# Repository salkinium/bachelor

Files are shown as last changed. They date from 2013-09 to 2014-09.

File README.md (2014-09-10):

Bachelor Thesis Source Code
===========================

This repository contains the entire source code of my bachelor thesis "Temperature Dependency of Bit Error Distributions in Wireless Sensor Networks".

Organisation
------------

This repository is organized as follows:

-	The *box* folder contains the PCB schematics and the CAD drawings and embedded software for the heat box,
- The *experiment_control* folder contains the python software for the experiment server and data logger,
- The *link_analysis* folder contains the python software for analyzing and visualizing experiment results,
- The *motes* folder contains the TinyOS source code for the WSN motes,
- The *position* folder contains CAD drawings of the WSN mote holder,
- The *thesis* folder contains the entire latex source code for my thesis.

[Thesis as PDF](https://github.com/salkinium/bachelor/raw/master/thesis/thesis.pdf).

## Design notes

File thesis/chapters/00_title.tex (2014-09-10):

\titlehead{
	\centering
	
	\hfill
	
} % end titlehead

\begin{titlepage}

\let\footnotesize\small \let\footnoterule\relax

\hbox{}
\vfill

\centering

\begin{doublespace} 
{ \huge\textbf{\textsf{Temperature Dependency \\ \vspace{-0.4em}
of Bit Error Distributions \\ \vspace{-0.4em}
in Wireless Sensor Networks \\ \vspace{-0.4em}}}}
\end{doublespace}
\vskip 2cm

{\large Bachelor Thesis\\[5pt]}
{\large \textbf{Niklas Hauser}}
\vskip 1cm

\textbf{RWTH Aachen University, Germany\\[5pt]
        Chair of Communication and Distributed Systems}
\vskip 2cm

\large

Advisors:
\vskip 2mm

\begin{tabular}{R{7cm}p{7cm}}
Dr. & Matteo Ceriotti\\
Dipl.-Inform. & Florian Schmidt\\
Prof.~Dr.-Ing. & Klaus Wehrle\\
Prof.~Dr.~rer.~nat. & Bernhard Rumpe
\end{tabular}
\vskip 1cm

\begin{tabular}{R{6cm}p{6cm}}
Registration date:  & January 29, 2014 \\
Submission date:    & May 29, 2014 \\
\end{tabular}

\vfill

\end{titlepage}

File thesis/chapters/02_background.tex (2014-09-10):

\chapter{Background}
\label{chap:background}

This work centers around investigating and improving the quality of corrupted communications in low power networks.
Therefore this chapter will provide the necessary background information on the form of communication used in \acl{WSN}s and the radio and microcontroller hardware we employed in our study.
Furthermore, we shortly describe what approaches to \acl{ECC}s exist and how they work.

\section{\acl{WSN}s}

A \acf{WSN} comprises of two or more nodes, called \emph{motes}, which can communicate using low power radio communication.
This provides a means to easily deploy sensing, actuating and communication infrastructures in a given space.
The nodes are mostly powered by small and simple microcontrollers connected to a radio and other peripherals such as sensors and actuators as shown in Figure~\ref{fig:mote_schematic}.

Networked motes communicate with their neighboring motes and can address the whole network via multi-hop transmissions, therefore deprecating the use of expensive wired buses.
However, due to the nature of wireless communication, the software must be built to tolerate unreliable communication links, which can change network topology and result in high latency in data exchanges or a complete loss of communication.

Integrated batteries are used to power the motes for a certain amount of time when deployed in areas where access to a power grid is too costly or impossible.
Especially for these battery powered applications, conserving energy is a high priority and places tight restrictions on the type of CPU and radio transmission power and duty cycle, effectively limiting communication range and bandwidth.

A typical application for a \ac{WSN} would be the collection of meteorological information over large inaccessible areas, such as forests, or the monitoring of large industrial complexes to reduce the cost of wiring~\cite{Boano2009}.
The high effort required to exchange empty batteries in these scenarios demands energy-aware programming, which keeps the overall energy consumption to a minimum.

\begin{figure}[t]
	\tikzset{
		boxt/.style={
	           rectangle,
	           fill=white,
	           draw=black, thick,
	           text width=2cm,
	           minimum height=1cm,
	           text centered},
	}
	\centering
	\begin{tikzpicture}[>=stealth',
	<->,
	shorten <=1pt,
	shorten >=1pt]
		% \draw (0,0) rectangle (7,5);
		\node[boxt, fill=slightgray] (controller) at (4, 4.3) {$\mu$Controller};
		\node[boxt] (sensors) at (5.7, 2.8) {Sensors};
		\node[boxt] (actuators) at (5.7, 1.7) {Actuators};
		\node[boxt, fill=slightgray] (radio) at (2.3, 1.7) {Radio};
		\node[boxt] (storage) at (2.3, 2.8) {Storage};
		\node (antenna) at (0.4, 3.5) {};
		\node[font=\small] (uart) at (6.35, 4.65) {UART};

		\draw (1,1) rectangle (7,5);
		\draw[thick] (1,0) rectangle (7,0.9) node[midway] {Power Source};

		\draw[thick] (controller.east) -| (sensors.north);
		\draw[thick] (controller.west) -| (storage.north);
		\draw[thick] ($(controller.south west)!0.45!(controller.south east)$) |- (radio.east);
		\draw[thick] ($(controller.south west)!0.55!(controller.south east)$) |- (actuators.west);
		\draw[thick, ->] ($(controller.south east)!0.8375!(controller.north east)$) -- (uart.west);

		\draw[very thick, -, shorten <=0pt, shorten >=-3pt] (radio) -| (antenna);
		\fill[color=black] (antenna) circle (0.075);
		\draw[dashed] (antenna) circle (0.15);
		\draw[dashed] (antenna) circle (0.25);
		\draw[dashed] (antenna) circle (0.35);
		\draw[dashed] (antenna) circle (0.45);

	\end{tikzpicture}
	\caption{A schematic representation of a mobile \acs{WSN} mote with a power source.}
	\label{fig:mote_schematic}
\end{figure}

\section{Communications}

Since this works focuses heavily on communications between motes, we use specific terms to help describe its properties.

A \emph{packet} is the basic unit of communication between two motes, containing metadata, such as sender and addressee, and payload.
A \emph{message} is the interpretation of the payload of one or several packets.
If a message is very long, it might be fragmented into several packets, however, in all our experiments, one message uses only one packet.
We define a \emph{link} as the transmission of messages from one mote addressed to another over a period of time, even when none of these messages where received by the addressee, due to channel effects or connection problems.

\subsection{IEEE 802.15.4 Standard}

In this work we use the CC2420 wireless transceiver~\cite{cc2420}, a very common communication radio in \acp{WSN}.
The CC2420 implements the \ac{IEEE} 802.15.4 standard and uses \ac{OQPSK} modulation in the \SI{2.4}{\giga\hertz} ISM band with a nominal data rate of \SI{250}{\kilo bit\per\second}.

The \ac{PPDU} is the lowest accessible layer as shown in Figure~\ref{fig:packet_format} with a maximum size of 133 bytes.
This leaves 127 bytes for the \ac{MPDU} and between 102 and 122 bytes for the frame payload.
To increase robustness of transmission, each byte is split into two 4-bit symbols, which are then mapped to a 32-bit chip sequence and modulated using \ac{OQPSK}.

These 32-bit chip sequences are part of \ac{IEEE} 802.15.4 and were chosen to produce high Hamming distances against each other, so that bit errors can already be corrected within the received chip sequence to some degree. 
The higher the Hamming distance between two sequences, the less likely they are to be mistaken for one another.
Therefore a corrupted 4-bit symbol is only received, when a corrupted chip sequence is mistaken for another sequence, which requires several bits of the 32-bit sequence to be flipped.
The minimum Hamming distance between two sequences is 12 bit, the maximum is 20 bit~\cite{Schmidt2013}.

At the beginning of every transmission, a Preamble Sequence is modulated, which triggers a listening mote to synchronize and receive this new packet.
Typical reasons for not receiving packets are either the reception of a signal with too little power to be noticeable above the channel noise, or the reception of a corrupted preamble, so that the listening mote does not start receiving a packet, even though the power levels would permit it.

When a packet is received, its \ac{FCS} is automatically evaluated to check for bit errors introduced by channel noise.
However, a failed \ac{FCS} test can also be the results of a corrupted Frame Length field.
This prompts the radio to read in too few or too many bytes, thereby comparing the \ac{FCS} results to the wrong bytes at, what the receiver wrongly considers the ``end'' of the packet.

Even though the \ac{FCS} is evaluated for all messages automatically, the CC2420 allows retrieval of corrupted messages, including all hardware link qualifiers such as \ac{LQI} and \ac{RSSI}.
We make use of this ability to analyze the content of these corrupted messages in our work.

\begin{figure}[t]
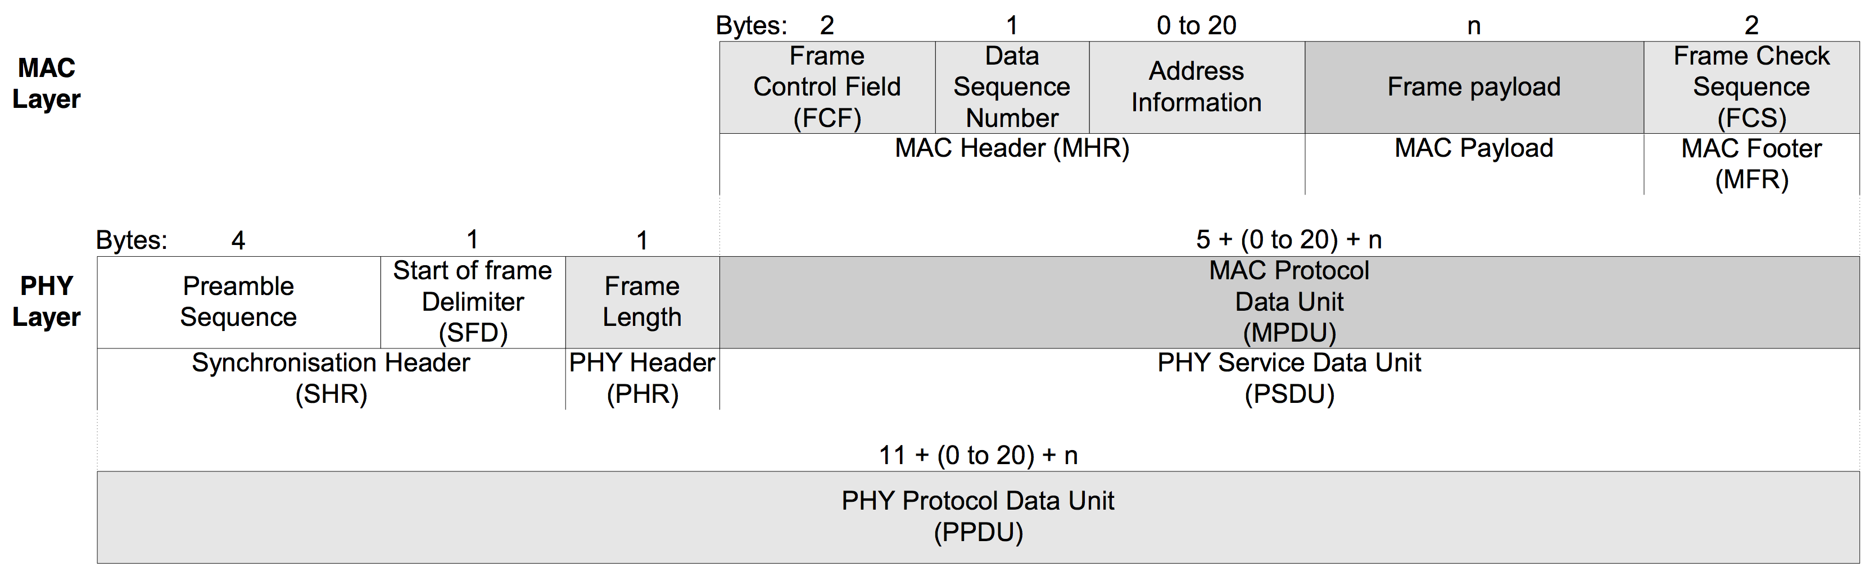
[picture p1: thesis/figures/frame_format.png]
	
	\caption{The packet format implemented defined by \acs{IEEE} 802.15.4 taken from \cite{cc2420}.}
	\label{fig:packet_format}
\end{figure}

\subsection{\acs{UART} Communication}

The microcontroller can also communicate over a wired bus using its \ac{UART} module.
\ac{UART} does not provide a seperate clock line (hence \emph{asynchronous}), which requires the receiver to synchronize itself at the beginning of each symbol transfer and sample the signal at multiples of the baudtime $t_{symbol} = f_{Clock} / f_{BaudRate}$, which derives from the \emph{baudrate} of the transmitter.
Here the receiver synchronizes on the falling edge of the start bit, which is always low, and has to sample the successive bits at the just right time, as shown in Figure~\ref{fig:uart_timing}.
If the transmitter's and/or receiver's clock is running too slow or too fast, then $t_{Symbol}$ is too small or too large, resulting in a corrupted sampling of the bits in the symbol as marked in red.

The relative error tolerance for the 8N1 configuration shown in the Figure (8 databits, 1 startbit and 1 stopbit) is $\pm5\%$, since the sample point of the stop bit may only shift by at most $\pm t_{Symbol}/2$.
With 10 bits to read, one $t_{Symbol}$ equals one tenth of the symbol transmission time, hence a relative tolerance of $\pm5\%$.
For example, the tolerance for 7-bit transfers (9 baudtimes) increases to $\pm5.56\%$.

However, since both transmitter and receiver may experience clock drift, the error must not exceed $5\%$ in total, which in the worst case of opposing clock drift directions (one too fast, one too slow) imposes a tight allowed deviation of $+2.5\%$ and $-2.5\%$ on the modules respectively.
In practice, \ac{UART} can therefore be difficult to use with uncorrected or unknown clock drifts.

\begin{figure}[t]
	% \centering
	\begin{tikzpicture}[thick, >=stealth']
		\draw[white] (-4.5,-0.75) -- (-3,-0.75);

		\def \di {0.46}
		\def \dii {0.535}

		\fill[slightgray] (1,2) rectangle (1.5,3) node[midway, black] {S};
		\fill[slightgray] (5.5,2) rectangle (6,3) node[midway, black] {P};

		\foreach \s in {0,...,7}
		{
			\draw (1.5+\s*0.5,2) rectangle (2+\s*0.5,3) node[midway] {\s};
		}

		\draw[-] (-1,3) -- (1,3) -- (1,2) -- (1.5,2);
		\draw[-] (5.5,3) -- (8,3);

		\path (-1,2) -- (1,3) node[midway, font=\tiny] {\textbf{IDLE}};
		\path (6,2) -- (8,3) node[midway, font=\tiny] {\textbf{IDLE}};

		\draw[->] (2.5,3.75) -- (7,3.75) node[midway, above, font=\small] {Time};

		\draw[->, shorten <=1pt, shorten >=1pt] (1,3.5) node[above, font=\small] {Sync} -- (1,3);

		\foreach \s in {0,...,9}
		{
			\filldraw (1.25+\s*0.5, 1.2) circle (0.06);
		}

		\draw[|<->|, shorten >=-0.4pt, shorten <=-0.4pt] (1,1.6) node[left=0pt, font=\small] {$t_{Symbol}$} -- (1.5,1.6);
		\draw[->, shorten >=3pt] (6.1, 1.65) node[right=0pt, font=\small] {Ideal Timing} -| (5.75, 1.2);

		\node[font=\small, right] at (-1,0.5) {Too Fast};
		\node[font=\small, right] at (-1,-0.2) {Too Slow};

		\fill[slightred, rounded corners] (1.25+\di*4.5+\di-0.5, 0.3) rectangle (1.25+\di*9.5+\di-0.5, 0.7);
		\foreach \s in {0,...,9}
		{
			\draw (1.25+\s*\di+\di-0.5, 0.5) circle (0.06);
		}

		\fill[slightred, rounded corners] (1.25+\dii*5.5+\dii-0.5, -0.4) rectangle (1.25+\dii*9.5+\dii-0.5, 0);
		\foreach \s in {0,...,9}
		{
			\draw (1.25+\s*\dii+\dii-0.5, -0.2) circle (0.06);
		}

		\foreach \s in {0,...,10}
		{
			\draw[line width=0.2pt] (1+\s*0.5,1.9) -- (1+\s*0.5,-0.6);
		}
	\end{tikzpicture}
	\caption{\acs{UART} timing diagram of the sampling points of an 8-bit symbol.}
	\label{fig:uart_timing}
\end{figure}

\section{Error Control Schemes}

There exist two approaches to improve the quality of an imperfect communication channel: using \ac{FEC} to add redundancy before transmission, so that bit errors can be \emph{detected} and \emph{corrected} by the receiver, and using \ac{ARQ} to only \emph{detect} bit errors, but request a retransmission, instead of correcting them.
While \ac{ARQ} is simple and requires very little computational and transmission overhead, it does perform poorly in conditions with a high channel error rate.
\ac{FEC} allows constant throughput at the expense of coding and decoding time and transmission overhead, depending on the specific \ac{ECC} used.
To overcome their individual disadvantages, these two approaches can be merged into \emph{hybrid} \ac{ARQ} schemes, however, in our work we will be focusing on using \ac{FEC} schemes alone.

The simplest \acp{ECC} belong to the class of linear cyclic coding schemes, where a bit stream is divided into non-overlapping blocks, which are then encoded separately.
The most widely used linear cyclic block codes are binary \ac{BCH} and non-binary \ac{RS} codes, both of which can be used to correct bit and burst errors.
There are several other approaches to \acp{ECC}, however, they go above the focus of this work.

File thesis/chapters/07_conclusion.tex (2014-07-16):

\chapter{Conclusion}

This work investigated the effects of temperature on bit error patterns and \ac{PRR} in the context of low power communications as used in \acp{WSN}.

We began with a description of the low-cost design of our testbed, which allows fine control of mote temperature, mote orientation and experiment execution.
This testbed was the foundation, which allowed us to create and control links with high \ac{BER} between CC2420 radios at different temperatures.
Due to problems with the serial communication between mote and PC, we measured microcontroller clock drift and found the \ac{DCO} calibration algorithm in TinyOS not to be working above \SI{55}{\celsius}, and provided and tested a correction method.

Then we showed that bit errors follow a distinct distribution, which is influenced by payload content, confirming findings by Schmidt~\etal~\cite{Schmidt2013} and extending them with a classification of pattern magnitudes.
We found two bit error patterns, which we did not know before, due to their rare occurrence.
Furthermore, we saw no influence of temperature on these patterns.

The experiments were completed with a detailed investigation into \ac{PRR} asymmetry, when transmitter and receiver were heated to different temperatures.
Our results showed that the receiver is more vulnerable to an increase in temperature than the transmitter, thereby disproving findings by Boano~\etal~\cite{Boano2013}.

We used these findings to create a trace-based simulator to study the effects of temperature on \ac{FEC} usage, and evaluated the simulators performance, which we found accurate.
Using traces of our real experiments, we simulated several \ac{RS} encoding strengths and compared them based on normalized throughput.
On this basis we proposed a minimum encoding strength of 12.5\% overhead, which is increased with temperature to a maximum of 25\% overhead.

% It seems we are missing a independent \ac{LQE} across platforms and testbeds.
% This exact problem has been summarized by Baccour~\etal{} in their survey~\cite{Baccour2012}.
% The authors come to the conclusions that of the hardware-based \ac{LQE}s, \ac{RSSI} has the worst accuracy, especially for intermediate links, and that \ac{LQI} is a better indicator of \ac{PRR} than \ac{RSSI}, as we have pointed out too.
% They come to the conclusion that software-based \ac{LQE}s are better at describing link quality than hardware-based \ac{LQE}s.

\newpage

\section*{Future Work}

The results of our experiment warrant further investigations into several topics.

In Section~\ref{sec:link_quality} we briefly described the difficulty we encountered in creating a link with the right \ac{BER} even when using our mote harness from Section~\ref{sec:mote_harness}.
An interesting addition to this harness could be a motor controlled z-axis to further automate link quality selection via antenna orientation in a closed-loop controller setup.
In that respect, it might be more practical to rebuild this harness partially out of LEGO Technic parts, which would make the mechanic aspects of this function much easier.

Concerning the limitations of the \ac{DCO} calibration algorithm of TinyOS described in Section~\ref{sec:clock_drift}, we filed a bug report on their open-source project page.
We hope that this raises awareness of the algorithm's performance and prompts a fix.

In Section~\ref{subsec:pattern_anomalies} we described two bit error patterns, which were very different to what we recorded in all other experiments we ran.
Further investigation is required to understand what creates these patterns and whether they exhibit different Hamming distances than described by Schmidt~\etal~\cite{Schmidt2013} and Hermans~\etal~\cite{Hermans2014}.

Further work is required to validate our proposals regarding temperature dependent \ac{RS} coding overhead using simulation and real experiments.
Even though our simulation was accurate enough for our conclusions, they were based on four real traces, which certainly do not cover all possible link qualities that can be expected in real world deployments.

% It is important to notice, that in regions with high link quality, especially at low temperature, \ac{ARQ} might outperform \ac{FEC} in energy efficiency as reported by Tian~\etal~\cite{Tian2008}.
% Therefore our results might be best deployed in a hybrid \ac{ARQ} scheme~\cite{Liu1997}, where \ac{FEC} is only deployed once the temperature reaches a certain threshold.

% \todo{we logged all raw data, so we could use it to test software-based \ac{LQE}s~\cite{Baccour2012}}

% \todo{Correlation threshold of the CC2420 can be user defined~\cite{Liang2010}}

% This link asymmetry can lead to some interesting situations, where a mote at high temperature is able to transmit messages, but not receive them.
% Looking at their own temperature, mote would receive another hint in whether the lack of received messages is caused by a missing transmitter, or by its own disability to receive messages.
% For example, when no messages are received after a timeout, a failure of the transmitter is more likely when the receiver is at low temperature than at high temperatures.

% In a system that makes smart decisions based on information from multiple motes, such information could be used to judge whether the system is still functionally intact and then trigger a backup program, which reacts autonomously to the local sensor data collected but still notifies the rest of the network of its actions.
% Motes that are not in this backup mode can very likely receive these transmissions and augment the group decisions with the constraints of these autonomously acting motes.
% Therefore a failure of the entire system is delayed or prevented, by using controlled degradation of the system, which might not be as smart as before, but at least still providing a rudimentary service.

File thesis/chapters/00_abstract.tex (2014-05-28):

\cleardoublepage

% \selectlanguage{german}

\begin{center}
\paragraph{Kurzfassung}
\hrulefill

\end{center}

Mit der Verfügbarkeit von leistungsfähigen eingebetteten Geräten und kostengün\-stigen Funkmodulen, beginnen auch immer mehr batteriebetriebene Sensorgeräte miteinander zu reden und Probleme gemeinsam zu entscheiden.
Es ist abzusehen, dass die Benutzung solcher intelligenten Geräte in drahtlosen Sensornetzwerken in\-dustrielle Prozesse vereinfachen und unsere Lebensqualität verbessern wird.

Allerdings ist die Laufzeit dieser mobilen Geräte durch ihre endliche Energiequelle, die meist nur mit viel Aufwand zu wechseln ist, beschränkt. Daher braucht es eine Programmierung, die energiebewusst kommuniziert, um die Lebensdauer der Bat\-terie so weit wie möglich zu verlängern.
Drahtlose Kommunikation ist stark durch Umweltveränderungen, allen voran die Lufttemperatur, beinflussbar, was zu Korrup\-tion oder Verlust von Paketen führen kann und ein erneutes Versenden des Pakets nach sich zieht.

In dieser Arbeit beschreiben wir eine kostengünstige Testplatform zum Testen der Funkverbindungen in einer temperaturkontrollierten Umgebung. Mit dieser Plat\-form untersuchen wir die Empfangsraten und die Bitfehlerverteilungen in korrupten Paketen.
Unsere Ergebnisse widerlegen frühere veröffentlichte Ergebnisse.
Schließ\-lich wenden wir diese Erkenntnisse auf die Programmierung eines Simulators an, mit dem wir untersuchen, wie sich Temperatur als Eingabegröße einer adaptiven Vorwärtsfehlerkorrektur verhält, um damit die Empfangsraten korrupter Pakete zu verringern.

% \selectlanguage{english}

\vspace {0.5cm}
\begin{center}
\paragraph{Abstract}
\hrulefill
\end{center}

With the availability of powerful embedded devices and inexpensive radio communication, ever more battery powered sensor devices make use of the added connectivity to talk to each other and decide problems collectively.
It is envisioned that usage of such smart devices in \acl{WSN}s will streamline industrial processes as well as improve our quality of life.

However, the runtime of these mobile devices is limited by their finite power source, which most often are impractical to exchange.
Therefore energy-aware programming and communication is required to prolong battery life for as long as possible.
Unfortunately, wireless communication is strongly influenced by environmental changes, most prominently air temperature, which can lead to packet corruption or loss and requires energy-consuming retransmissions.

In this work we describe a low-cost testbed for testing radio performance in a temperature-controlled environment, with which we examine packet reception rates and bit error distributions within packet corruption. Our results disprove previous published findings.
Finally, we apply these findings on building a simulator, with which we investigate using temperature as an input for an adaptive \acl{FEC} scheme to improve packet reception rates and thereby reduce unnecessary retransmissions.

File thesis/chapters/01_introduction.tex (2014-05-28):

\chapter{Introduction}

With the introduction of more powerful low-power embedded devices, such as small microcontrollers, and the increased availability of low-cost radio transceivers especially in the last decade, more and more applications have been developed that enrich their functionality by receiving input from our environments.
Such applications can help us to use natural resources, such as farm land or forests, more efficiently, or streamline industrial processes by retrofitting more data sampling points, or simply alarm us when we forget to water the plants at home.

Concepts of augmenting our environments with connected sensors and actuators have been talked about for many years, with the most prominent concept being the \ac{IoT}.
Here everyday objects are able to communicate with each other over local networks or the Internet and come to smart decisions collectively.
This infusion of information about the real into the virtual world will keep growing with many new and exciting ways to improve our quality of life.

However, these concepts are built on very new technology, which has to be understood to be improved for the next generation of such devices.
The common culprit of today's mobile devices are their battery lives.
Even though impressive advancements have been made, especially in the area of smart phones, charging or exchanging batteries is cumbersome at best, and, in regard to sensor devices, impractical when they are distributed over large areas.
It is therefore imperative to extend battery life for as long as possible, which means not only using low-power hardware, but also merging it with energy-efficient software.

Fortunately, long and intensive computations do not have to be performed on the sensor devices locally, but can be delegated to a server connected to the power grid.
For that however, the sensor nodes must communicate using radio communication, which is by the laws of physics and electrical engineering still inherently energy-inefficient, especially compared to wired communication.

What sounds simple actually is complicated by the fact that radio communication is at the mercy of the environment, which introduces noise into the signal and strongly influences signal propagation.
Further complications arise with different antenna designs, the limitations of the modulation scheme and non-linearities in analog circuitry.
This leads to packets being corrupted or not being received at all, requiring the retransmissions of the original packet until it is received error-free.
However, in conditions of poor link quality this might not even be possible.
Hence, to reduce energy consumption, radio communication, especially retransmissions, must be kept to a minimum while not impairing functionality of the original application.

Additionally, a typical \acl{WSN} is deployed outside and its nodes are protected by air-tight containers from precipitation.
On a sunny day, temperatures inside these containers can climb well above outside air temperature, which influence radio and microcontroller performance quite dramatically.
In this thesis we focus on what impact temperature has on patterns in packet corruption and describe the experiments we created to study these patterns.
We analyze the results and try to improve link quality using \acl{FEC}.

The main contributions of this thesis are:
\begin{enumerate}
  \item
  the creation of a low-cost testbed for testing radio performance in a temperature-controlled environment (Chapter~\ref{chap:testbed}),
  
  \item
  the investigation of microcontroller clock drift, and the limitations of its calibaration in TinyOS (Chapter~\ref{chap:experiments}),

  \item
  the detailed analysis of the effects of temperature on bit error patterns and \acl{PRR}, which disproves published findings by Boano \etal~\cite{Boano2013} (Chapter~\ref{chap:experiments}),
  
  \item
  the modeling of the discovered patterns using a simulator (Chapter~\ref{chap:forward_error_correction}), and

  \item
  the investigation of using an adaptive \acl{FEC} scheme to improve throughput in temperature-influenced link conditions (Chapter~\ref{chap:forward_error_correction}).
\end{enumerate}

We provide the necessary background knowledge required for understanding our work in in Chapter~\ref{chap:background}, before briefly discussing previous, related work in Chapter~\ref{chap:related_work}.

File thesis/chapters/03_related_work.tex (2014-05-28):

\chapter{Related Work}
\label{chap:related_work}

The research field of investigating influences of the environment on wireless link quality is large and spans many technologies and protocols.
However, we focus on technologies deployed in low power networks such as \ac{WSN}s, where the advances in small and affordable radio technology pushed research forward.
In a first step towards energy efficient, reliable communications, especially in battery powered applications, a deep understanding of why messages become corrupted is required.

Here we present research relating to the IEEE 802.15.4 protocol used in most \ac{WSN}s, especially in the three areas this work focuses on, namely, the influence of temperature on link quality and bit error distributions within corrupted messages, as well as the use of \ac{FEC} to counteract these effects.

\section{Effects of Temperature}

Bannister~\etal~\cite{Bannister2008} were one of the first to systematically investigate the effect of temperature on the performance of the CC2420 radio.
They connected two radios together via coaxial cable with attenuators and placed one of them in a thermal chamber with a temperature range of 25 to \SI{65}{\celsius} while measuring signal power using the \ac{RSSI}.
The results showed a reduction of output power by $4--$\SI{5}{\dBm} when the transmitter was heated, but only \SI{3}{\dBm} reduction in measured input power when the receiver was heated.
Boano~\etal~\cite{Boano2010} also investigated this behavior in 2010 in a real world deployment, but found no difference in \ac{RSSI} between transmitter and receiver.
However, both works point to a loss of gain in the CC2420 \ac{LNA} as the source of the reduction in signal powers at higher temperatures.

In a long-term outdoor study in 2013, Wennerstr{\"o}m~\etal~\cite{Wennerstrom2013} examined the correlation between \ac{RSSI} and \ac{PRR} and environmental factors, such as temperature, relative and absolute humidity, precipitation and sunlight.
They found that of all environmental factors, temperature had the strongest influence, with an increase in temperature causing a significant decrease in both \ac{RSSI} and \ac{PRR}.
This was further researched by Boano~\etal~\cite{Boano2013}, who focused on the impact of temperature on \ac{RSSI}, \ac{SNR}, Noise Floor, \ac{PRR} and \ac{LQI}.
They determined a negative impact of temperature on all these values and expanded their work by looking at the asymmetry of \ac{PRR} when heating the transmitter and receiver.
They found that the loss in \ac{PRR} was more pronounced when heating the transmitter than the receiver.

Finally, Z\'{u}\~{n}iga~\etal~\cite{Zuniga2013} created a summarizing report on the effect of environment variables on current \ac{WSN} motes.
Apart from including all previous findings, they also describe a substantial negative impact of temperature on microcontroller clock drift.
However, the CC2420 clock is compensated for temperature and experiences no such drift.

\section{Bit Error Distributions}

Liang~\etal~\cite{Liang2010} investigated bit error distributions in the context of 802.11 (WiFi) interference.
They found that packet collisions cause burst errors, due to 802.11 packets typically being much shorter than 802.15.4 packets, particularly in the beginning of a message.
This is due to the 802.11 sender deferring sending its packets until the 802.15.4 transmission completed, however only if the 802.15.4 sender is close enough so that its transmission power can be sensed by the 802.11 collision avoidance algorithm.
If the 802.11 sender cannot sense the 802.15.4 transmission, the authors show an even bit error distribution across the entire packet.

Schmidt~\etal~\cite{Schmidt2013} examined the bit error distributions within corrupted messages in their outdoor testbed of 20 TelosB devices.
Similar to Liang~\etal, they found that for random payload, \ac{BER} remains stable throughout message, however, within all 4-bit symbols, the \ac{MSB} is significantly less likely to break than the 3 \ac{LSB}.
In addition, symbols with \ac{MSB} set to 1 are more likely to break than symbols with \ac{MSB} set to 0.
This behavior creates very different Hamming distances between the broken symbols coded in 32-bit chip sequences than defined by the 802.15.4 standard.
The authors also looked at burst error distribution and found these errors not independently distributed, but skewed towards longer bursts.

Their findings then where further completed by Hermans~\etal~\cite{Hermans2014} with an understanding of why the Hamming distances are different than expected.
The authors discovered that the pattern fits, when their simulation of these patterns uses a \ac{MSK} instead of the \ac{OQPSK} demodulator suggested by the 802.15.4 standard.
The \ac{MSK} demodulator can correctly receive packets sent by an \ac{OQPSK} modulator, but it outputs different code words than defined by the standard.
The authors hypothesized that these code words then have to be translated using a table, which would create the distinct bit error patterns.

\section{\acl{FEC}}

The use of \ac{FEC} schemes in communication has been investigated before, however, the available limited resources on \ac{WSN} motes focus research in this area very much on coding and energy efficiency.

Jeong~\etal~\cite{Jeong2003} investigated the performance of single- and double-bit correcting \ac{ECC} on very early \ac{WSN} motes, not using the 802.15.4 standard.
They came to the conclusion, that using \ac{BCH} codes is simple to implement, but performs poorly when encountering burst errors.
Busse~\etal~\cite{Busse2006} then compared the performance of a Hamming code, an interleaved double-bit correction code and a \ac{RS} code using their \ac{WSN} and found the \ac{RS} code to be the most efficient of them, both in the length of the added overhead, as well as the error correction capabilities.

Using mathematical energy consumption modeling, Tian~\etal~\cite{Tian2008} showed that for small packet lengths ($<1023$ bytes) \ac{BCH} codes outperform \ac{ARQ}.
However, research by Ma~\etal~\cite{Ma2009} points to \ac{RS} being more energy efficient than \ac{BCH} codes, especially when considering the energy consumption of transmitting the coding overhead.

Ahn~\etal~\cite{Ahn2005} examined changing \ac{FEC} coding strength dynamically based on link quality properties.
Their adaptive \ac{FEC} algorithm outperformed several static \ac{RS} codes in simulation, as well as in real traces.
Liang~\etal~\cite{Liang2010} created and evaluated an efficient, TinyOS compatible \ac{RS} implementation, called TinyRS, during their research on bit error distributions mentioned before.

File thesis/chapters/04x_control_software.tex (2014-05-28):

\section{Control Software}
\label{sec:control_software}

The motes and temperature boxes are connected via USB-to-Serial converters to a computer, and controlled with a Python program using the TinyOS Python SDK~\cite{tinyos.net}.
Since all motes are connected to one computer, packet loss due to colliding transmissions is avoided via central scheduling of transmissions.
The software holds virtual representations of the mote, temperature controller and link, and logs experiment results to disk.
A simple scripting language allows the definition of commands that are interpreted by the runtime and executed serially so that experiments can be described in independent and compact form.
Multiple scripts can be added, so that experiments can run unsupervised around the clock.

During an experiment all transmissions and receptions are written to a log in ASCII format, which includes a timestamp, sending and receiving node ids, a sequence number, link quality metadata, mote temperature and the entire \ac{MPDU} payload, including \ac{FCS}.%, as shown in Listing~\ref{lst:log_example}.
These logs describe the entire experiment in a unprocessed format, which is then read by the evaluation scripts that reassemble them into messages and links.

This modular software setup allows for a lot of freedom when designing these experiments, as all evalutation data is based upon these unprocessed logs.
This enables us to use one experiment for multiple purposes by focusing on different parameters, of which we will make use later in in Chapter~\ref{chap:forward_error_correction}.

\begin{listing}[t]
\begin{lstlisting}[breaklines=true]
timestamp=2014-05-03 09:22:21,752	mode=tx	id=0	seqnum=0	temperature=29.9	length=93	data=[...]	power=3
timestamp=2014-05-03 09:22:21,753	mode=rx	id=1	seqnum=0	temperature=33.0	timeout=1

timestamp=2014-05-03 09:22:21,890	mode=tx	id=1	seqnum=1	temperature=33.0	length=93	data=[...]	power=3
timestamp=2014-05-03 09:22:21,890	mode=rx	id=0	seqnum=1	temperature=29.9	length=93	data=[...]	rssi=-90	lqi=104 crc=1 timeout=0
\end{lstlisting}
\caption{A log excerpt showing two transmissions, of which the first reception timed out. The raw data field is ommited for clarity.}
\label{lst:log_example}
\end{listing}

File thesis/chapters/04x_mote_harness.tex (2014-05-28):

\section{Mote Harness}
\label{sec:mote_harness}

In order to guarantee that both sender and receiver will not move during experiments a mote harness was developed and laser cut out of acrylic.
The mote snaps into the harness so that the axis of rotation goes through the middle of the PCB antenna which then allows rotation in \SI{5}{\degree} steps as shown in Figure~\ref{fig:mote_harness}.
Furthermore, the distance between two harnesses can be adjusted in \SI{5}{\milli\metre} steps using laser-cut wooden distance bars.

In our experiments this greatly improved the handling of the motes. Where before we used to tape the mote down into position, which was an inaccurate matter at best, we now have a simple and elegant solution.
However, we ended up not actually using the distance bars in most of our experiments, as it was simpler to use antenna orientation to control link quality than distance.
Therefore, in Figure~\ref{fig:box_hardware_picture} the mote harness is fixed onto the baseplate.

\begin{figure}[t]
	\subfigure[Harness with mote on a distance bar.] {
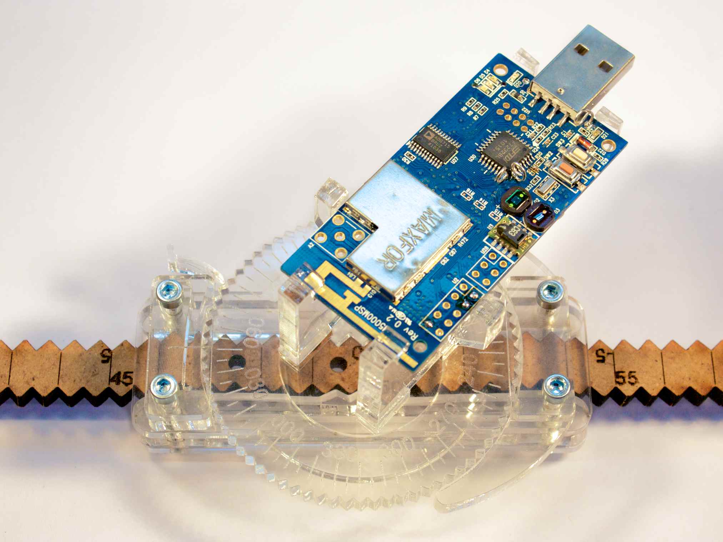
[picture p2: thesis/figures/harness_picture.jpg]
		
		\label{fig:harness_picture}
	}
	\subfigure[Vector drawing of the rotation disc.] {
		
		\label{fig:harness_vector}
	}
	\caption{The mote harness allows precise positioning of motes.}
	\label{fig:mote_harness}
\end{figure}

% \newpage

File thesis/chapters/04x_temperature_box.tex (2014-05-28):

\section{Temperature Box}
\label{sec:temperature_box}

For our experiments we needed a way to accurately control temperature of motes in our \ac{WSN}.
Even though previous setups used an infrared lamp~\cite{Boano2014, Hermans2013} to heat the motes directly, we chose to control mote temperature only using air temperature.
The mote is placed in a closed \ac{PS} hard-foam box and the confined air is heated to the requested temperature and circulated to transfer this heat to the mote.
The box has the outside dimensions of \SI{35 x 35 x 30}{\centi\metre} with a wall thickness of \SI{5}{\centi\metre} which results in a holding capacity of \SI{12.5}{\litre}.

\subsection{Hardware}
A microcontroller evaluates temperature sensors within the box and locally controls the duty cycles of a small fan and a \SI{150}{\watt} ceramic heating element using a closed-loop \acs{PID} controller to achieve the requested air temperature.
The microcontroller can communicate over a serial connection to receive the desired temperature and send the current temperature.

Additionally, air temperature is displayed as a hue from blue (cold) via green (warm) to red (hot) on a RGB LED.
The duty cycles of the heating element and fan are mapped to two white LEDs, to provide an immediate status overview and prevent burn injuries.

The box is powered by a \SI{300}{\watt} PC power supply, which was chosen for its ability to provide \SI{12}{\volt}, \SI{5}{\volt} and \SI{3.3}{\volt} at the required currents, which removes the need for additional (costly) voltage conversion.
A custom designed PCB distributes power from the \acs{ATX} connectors to two high and two medium power \acs{MOSFET} switches and up to five temperature sensors, all controlled by an ATmega328.

The PCB, heating element and fan are fixed on a wooden baseplate shown in Figure~\ref{fig:box_hardware_picture} using custom fasteners and standard screws.
All custom made parts were prototyped using the PCB mill and laser cutter of the RWTH FabLab~\cite{fablab}.

\begin{figure}[t]
	\centering
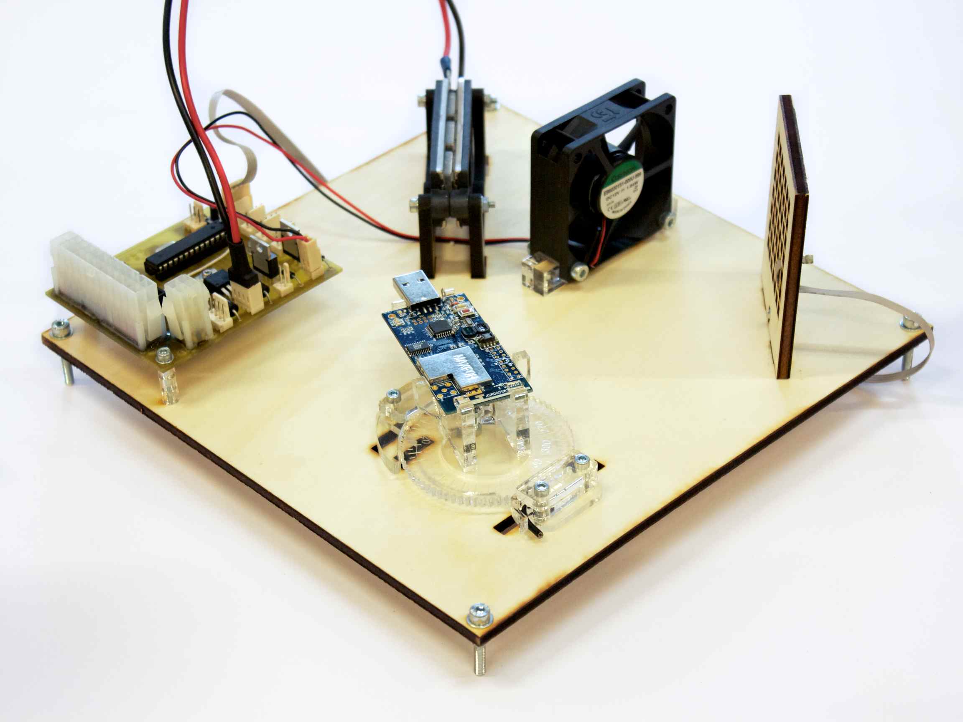
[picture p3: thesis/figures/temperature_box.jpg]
    
	\caption{Baseplate with temperature controller, heating element, fan and sensor mote.}
    \label{fig:box_hardware_picture}
\end{figure}

\subsection{Embedded Software}

The embedded software is written in C++ using the xpcc microcontroller framework~\cite{xpcc.io} and implemented as a set of asynchronous control tasks for input parsing and output formatting, temperature sensor evaluation, \acs{PID} loop update and duty cycle generation.
The choice of an ATmega328 as a microcontroller was deliberate to enable compatibility with the Arduino framework, which might be more familiar to developers.

Once the controller is programmed via \ac{ISP}, it will periodically send the values of all attached temperature sensors, as well as the current heating element power setting in human-readable ASCII format.
Desired temperature can be sent as an ASCII formatted integer followed by the letter `C'.
All switching frequencies were kept well below \SI{1}{\kilo\hertz} to avoid any kind of interference with the \SI{2.4}{\giga\hertz} band.

\subsection{Performance}

The heating element has enough power to heat the air inside the box up to \SI{120}{\celsius}.
This can however damage both the \ac{PS} material as well as the mote, so a hard limit of \SI{90}{\celsius} is imposed during experiments.

As seen in Figure~\ref{fig:box_heating_cooling} it takes about 40 minutes to heat up to \SI{90}{\celsius} and about 2 hours to cool back down to \SI{30}{\celsius}.
The \acs{PID} loop is deliberately dampened so that no overshoot in air temperature occurs, however, since the mote temperature naturally lags behind, a slight overshoot in air temperature might actually help achieve desired mote temperature quicker.
However, during the experiments a more granular approach is used similar to Figure~\ref{fig:box_heating_step}.

The boxes can be retrofitted with an active piezoelectric cooling element and a fan by connecting them to the two unused \acs{MOSFET} switches on the controller and updating the software, which also allow reaching temperatures below room temperature.
Since we did not use a cooling element, we set the minimum experiment temperature at \SI{30}{\celsius} so that in a room temperature of $20-$\SI{25}{\celsius} it can still be reached within reasonable time.

\begin{figure}[t]
	\subfigure[Heating to \SI{90}{\celsius}, then cooling to \SI{30}{\celsius}.] {
    	
    	\label{fig:box_heating_cooling}
    }
    \subfigure[Temperature increments of \SI{5}{\celsius}.] {
	    
	    \label{fig:box_heating_step}
	}
	\caption{Typical performance of the boxes over time. Notice the mote temperature (red line) lagging behind air temperature (green line).}
	\label{fig:box_heating_curves}
\end{figure}

Compared to TempLab by Boano~\etal~\cite{Boano2014}, which uses infrared heat lamp controlled via the wireless Z-Wave home automation protocol, our boxes require more manual assembly, do not operate wirelessly and cannot change temperature as fast.
However, our boxes also only cost one third as much (\EUR{91} versus \EUR{293}).

% \newpage

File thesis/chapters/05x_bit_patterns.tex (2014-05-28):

\section{Patterns in Bit Error Distributions}
\label{sec:bit_error_patterns}

We designed two experiments to investigate the results of Schmidt~\etal~\cite{Schmidt2013}.
The first experiment was used to confirm their findings and also investigate the influence of hardware layout on \ac{BER} patterns, while the second experiment investigated the influence of temperature on these patterns.

\subsection{Effects of Board Layout}
\label{subsec:effects_of_board_layout}

In all our experiments we used Tmote Sky motes, which are commercial drop-in replacements for the original Telos mote design by Polastre~\etal~\cite{Polastre2005}.
We had hardware revisions available from two manufacturers: the original design from (now defunct) MoteIV Corporation and the Maxfor MTM-CM5000MSP, which uses a slightly different schematic and board layout.
Notable differences include the \SI{3}{\volt} regulator and the physical layout of the radio circuitry.

In the experiment a pair of CM5000 and original motes transmitted to two CM5000 and two original motes.
All motes were powered by the on-board voltage regulator via the USB connector, which was also used to establish serial communications with the PC.
This redundant placement shown in Figure~\ref{fig:8mote_experiment_setup} was chosen so that the same transmission was received by both types.
Over the course of six days the four transmitters sent 563,500 messages each, totaling 2,254,000 transmitted messages at power setting 2 (below \SI{-25}{\dBm}).
Since each transmission was sent to four receivers, a total of 9,016,000 receptions should have been possible.
Of those 5,280,369 were received and 2,497,744 had at least one bit error.
The experiment was located in the large climate-controlled server room in the basement, where the temperature remained within $20$--\SI{25}{\celsius} with no other changes in the environment.

\begin{figure}[t]
	\centering
	\begin{tikzpicture}
		\newcommand\receiver[5]{%
		    \begin{scope}[xshift=#1cm,yshift=#2cm,rotate=#3]
		        \draw[fill=#4] (0,0) rectangle (1,2.1);
		     	\draw[fill=black!10] (0.33,0.1) rectangle (0.66,-0.45);
		     	\draw[snake=snake, white, segment amplitude=1.75, segment length=5, line width=1.25pt] (0.1, 1.95) -- (0.9, 1.95);
		     	\node at (0.5cm, 1.05cm) {#5};
		    \end{scope}
		}
		\newcommand\transmitter[5]{%
			\receiver{#1}{#2}{#3}{#4}{#5};
		    \begin{scope}[xshift=#1cm,yshift=#2cm,rotate=#3]
		     	\draw[snake=expanding waves, segment angle=40, segment length=7] (0.5,2) -- (0.5,3);
		    \end{scope}
		}

		% new = red, old = blue
		% new transmitter
		\transmitter{3}{7}{-65}{motered}{0};
		\transmitter{3.675}{5.5}{-65}{motered}{1};		

		% new transmitter
		\transmitter{0}{2}{-65}{moteblue}{2};
		\transmitter{0.675}{0.5}{-65}{moteblue}{3};

		\receiver{13}{0}{180}{motered}{7};
		\receiver{13}{3}{180}{moteblue}{6};
		\receiver{13}{6}{180}{motered}{5};
		\receiver{13}{9}{180}{moteblue}{4};

		% labels
		\node at (3, 7.75) {CM5000};
		\node at (0, 2.8) {Original};

		\node at (3, -1.5) {Transmitters};
		\node at (10.5, -1.5) {Receivers};
	\end{tikzpicture}
	\caption{Experiment setup with four transmitters and four receivers.}
	\label{fig:8mote_experiment_setup}
\end{figure}

The CM5000 motes required to be physically closer to the receivers at the same power setting to have similar link quality as the original motes.
This might be hinting at a difference in range between the two hardware layouts, however, our experiment was not set up to systematically investigate range.

In the initial evaluation we noted some significant differences in the quality of some links, where the co-located transmitters are sending to the same receiver.
For example, the link 3--5 is of very good quality with over 99\% \ac{PRR}, however link 2--5 shows quite the opposite with less than 1\% \ac{PRR}, even though both transmitters are located at the same distance and angle from the receiver.
This confirms the findings of Baccour~\etal~\cite{Baccour2012}, specifically that link quality is anisotropic, \ie the communication range exhibits a non-spherical pattern.
More exhibitions of this behavior can be found in the complete table of link qualifiers in the Appendix as Table~\ref{tab:8mote_link_qualities}.

Further analysis revealed the same bit and symbol error patterns as first discovered by Schmidt~\etal~\cite{Schmidt2013}, which state that within any transmitted symbol, the first three \acp{MSB} are more likely to break than the \ac{LSB} and that symbols 8--15 with the \ac{MSB} set to 1 are more likely to break than 0--7.
The normalized occurance of bit errors are plotted in Figure~\ref{fig:8mote_bit_errors}, with the first 12 bytes (96 bits) consisting of the message header with partially fixed content and the remaining 80 bytes are the constant payload, made up of two 32 byte patterns of 0x0000, 0x1111, $\ldots$ 0xFFFF, and one 16 byte pattern of 0x00, 0x11, $\ldots$ 0xFF.

\begin{figure}[t]
	\subfigure[XL] {
    	
    	\label{fig:8mote_bit_errors_xl}
    }
    \subfigure[L] {
	    
	    \label{fig:8mote_bit_errors_l}
	}
	\subfigure[M] {
	    
	    \label{fig:8mote_bit_errors_m}
	}
	\subfigure[S] {
	    
	    \label{fig:8mote_bit_errors_s}
	}
	\caption{Four magnitudes of \acs{BER} patterns with fixed payload of twice 0x0000, 0x1111, $\ldots$ 0xFFFF and once 0x00, 0x11, $\ldots$ 0xFF. The message header is indicated in gray.}
	\label{fig:8mote_bit_errors}
\end{figure}

We were able to confirm the findings of Schmidt~\etal{} and extend them with a classification of the influence of symbols on \ac{BER}.
The Subfigures in \ref{fig:8mote_bit_errors} show four magnitudes of this phenomenon, ranging from an extreme to almost no difference between symbols, named XL, L, M and S.
The remaining links can be classified into these four categories as done in Table~\ref{tab:8mote_bit_error_link_classification}.
XL and L patterns seems to be more common than M and S, with 8 vs. 3 links respectively, however, the table is incomplete, since only 11 out of 16 links had enough bit errors to recognize and categorize the pattern.

Schmidt~\etal{} also looked into the burstiness of errors and showed in their research that burst errors are not independently distributed.
The authors explained the drop from 4-bit bursts to 5-bit bursts with the added difficulty of corrupting a minimum of 7 bits to overcome the minimum Hamming distance of 12 between two symbol's chip sequences.
They also hypothesized that a similar drop would occur between 8-bit and 9-bit bursts, but were unable to confirm this, due to their limited sample size.
With our larger sample size we can confirm their hypothesis, with the drop quite noticeable in Figure~\ref{fig:8mote_xl_burst}.

\begin{table}[ht]
	\begin{tabularx}{\linewidth}{|c*{4}{|c}|}
	\hline
	\T \cellcolor{slightgray} Receiver	& \multicolumn{1}{X|}{\cellcolor{motered} \centering Sender 0} & \multicolumn{1}{X|}{\cellcolor{motered} \centering Sender 1} & \multicolumn{1}{X|}{\cellcolor{moteblue} \centering Sender 2}	& \multicolumn{1}{X|}{\cellcolor{moteblue} \centering Sender 3}\\
	\hline

	\cellcolor{moteblue}\T 4 & S  & \cellcolor{slightgray} & \cellcolor{slightgray} & \cellcolor{slightgray}   \B\\
	\hline
	\cellcolor{motered}\T  5 & XL & XL & L & XL \B\\
	\hline
	\cellcolor{moteblue}\T 6 & XL & L  & M & \cellcolor{slightgray}   \B\\
	\hline
	\cellcolor{motered}\T  7 & L  & \cellcolor{slightgray} & S & L  \B\\
	\hline 
	\end{tabularx}

	\caption{Classification of all links with enough absolute bit errors (otherwise gray).}
	\label{tab:8mote_bit_error_link_classification}
\end{table}

\begin{figure}[t]
	\subfigure[XL burst error distribution.] {
    	
    	\label{fig:8mote_xl_burst}
    }
    \subfigure[S burst error distribution.] {
	    
	    \label{fig:8mote_s_burst}
	}
	\caption{The burst error distributions of XL and S magnitudes show more longer burst errors in S magnitude. The error bars denote 99\% confidence intervals.}
	\label{fig:8mote_burst_error}
\end{figure}

We cannot see any correlation between the four \ac{BER} pattern classifications and burst error distribution or any other variable.
We therefore believe the magnitude of these patterns to be a result of the analog circuits of the radio, something that cannot be changed or improved by software.

\subsection{Effects of Temperature}
\label{subsec:effects_of_temperature}

To investigate the influence of temperature on \ac{BER} patterns, we used the CM5000 motes in the temperature boxes as described in Section~\ref{sec:temperature_box}.
To minimize signal disturbance we mounted the boxes in the storage room on wooden posts, so that they were floating in free space.
We placed the boxes at a fixed distance of \SI{280}{\centi\metre} to each other and controlled link quality sorely by rotating the antenna.

We ran three experiments with the same constant payload as described in the Subsection~\ref{subsec:effects_of_board_layout} but with power setting 3 (\SI{-25}{\dBm}) at \SI{30}{\celsius}, \SI{50}{\celsius} and \SI{70}{\celsius}.
Due to the decrease of link quality at higher temperatures, discussed in detail in Section~\ref{sec:packet_reception_rate}, we had to adjust mote rotation to regulate \ac{BER} at these temperatures, therefore small differences in absolute bit errors are present.
However, Figure~\ref{fig:temperature_bit_errors} shows no significant difference between \ac{BER} patterns at all three temperatures and therefore we did not pursuit this further.

\begin{figure}[t]
	\subfigure[\acs{BER} pattern at \SI{50}{\celsius}.] {
    	
    	\label{fig:temperature_bit_errors_30}
    }
    \subfigure[\acs{BER} pattern at \SI{70}{\celsius}.] {
	    
	    \label{fig:temperature_bit_errors_70}
	}
	\caption{\acl{BER} patterns show no difference between \SI{30}{\celsius}, \SI{50}{\celsius} and \SI{70}{\celsius}. The pattern at \SI{30}{\celsius} is omitted, since it is redundant.}
	\label{fig:temperature_bit_errors}
\end{figure}

\subsection{Pattern Anomalies}
\label{subsec:pattern_anomalies}

Even though the vast majority of experiment evaluations confirmed these patterns, there were two runs with  drastically different outcome.
We were very surprised to find a second, completely opposite \ac{BER} pattern as shown in Figure~\ref{fig:anomalie_bit_error}.
Here the symbols 0-7 show a higher average \ac{BER} and a less pronounced 4-bit saw-tooth pattern than symbols 8-15.
The pattern almost looks like an ``inverse'' of those described earlier.

The first time it occurred, we attributed this to influences of the environment and discarded it.
Two months later, this pattern occurred again with different hardware in a different setup in a different environment.
Both times, the motes were exposed to high temperature (>\SI{70}{\celsius}) over several hours, however, we were unable to confirm if this indeed triggered the pattern.
This pattern remained for days, regardless of temperature, link quality or message payload.

We cannot envision a source of interference capable of fundamentally changing this \ac{BER} distribution and neither does a permanent change of the radio chip's hardware at high temperature seem possible.
The CC2420 radio is rated to be operated at temperatures up to \SI{85}{\celsius} and to be stored at up to \SI{150}{\celsius}, while our experiments where limited to at most \SI{90}{\celsius} for a few hours.

Since we could not find any other reference to this pattern in literature and due to the rarity of this occurrence in our experiments and the difficulty of its repeatability, we decided to focus on investigating the ``normal'' patterns.

\begin{figure}[t]
	\subfigure[First occurance.] {
    	
    	\label{fig:anomalie_earlier}
    }
    \subfigure[Second occurance.] {
	    
	    \label{fig:anomalie_later}
	}
	\caption{``Inverted'' \acs{BER} pattern anomaly of constant data. Only the first two 32 byte patterns are shown.}
	\label{fig:anomalie_bit_error}
\end{figure}

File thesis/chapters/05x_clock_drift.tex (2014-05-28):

\section{Microcontroller Clock Drift}
\label{sec:clock_drift}

The Tmote Sky uses a MSP430 microcontroller clocked by an integrated ring oscillator called the \ac{DCO}.
Since the generated clock frequency varies from chip to chip with temperature and operating voltage, the \ac{DCO} can be fine-tuned in software using a modulation functionality.
During booting, TinyOS calibrates the \ac{DCO} using the external low-current \SI{32.756}{\hertz} watch crystal to generate a more accurate \SI{1}{\mega\hertz} clock.
It should be noted, that by default calibration only occurs after a reset, and not periodically during program execution.

We noticed that serial communication stopped working after heating the nodes above $55-$\SI{60}{\celsius}. Below this temperature the problem could be mitigated by resetting the mote to trigger a recalibration of the \ac{DCO}.
Boano~\etal{} reported similar synchronization trouble in their TempLab setup~\cite{Boano2014}.
We therefore looked at the output of the \ac{UART} module with a logic analyzer and measured how the selected baudrate changed over temperature.
The \ac{UART} receiver can tolerate up to $\pm5\%$ relative error, however, with the relative errors of several baudrates reaching well over $-20\%$ as shown in Figure~\ref{fig:baudrate_error}, resynchronization is impossible.

Since the baudrate is generated by scaling the \ac{DCO}, the \emph{relative} baudrate error is equivalent to \emph{relative} \ac{DCO} error over temperature.
We calculated an average temperature clock drift coefficient of \SI{-0.367}{\%\per\celsius}, which is within the typical range according to the datasheet. Similar coefficients were found by Z{\'u}{\~n}iga~\etal~\cite{Zuniga2013}.

\begin{figure}[t]
	\subfigure[Relative error of four baudrates.] {
    	
    	\label{fig:baudrate_error}
    }
    \subfigure[Relative error of \acs{DCO} calibration.] {
	    
	    \label{fig:reboot_drift}
	}
	\subfigure[Relative error of corrected baudrate.] {
	    
	    \label{fig:baudrate_look_up_error}
	}
	\subfigure[Values of baudrate correction look-up table.] {
	    
	    \label{fig:baudrate_look_up}
	}
	\caption{\acs{UART} and \acs{DCO} calibration errors over temperature. The dotted gray line indicates $\pm5\%$ \acs{UART} tolerance.}
\end{figure}

We then measured the relative baudrate error after rebooting over temperature.
As shown in Figure~\ref{fig:reboot_drift}, the TinyOS implementation of the \ac{DCO} calibration only works until \SI{55}{\celsius}, after which it has no corrective effect on CPU frequency, making periodic \ac{DCO} calibration during program execution ineffective.
It is possible that Contiki OS~\cite{contiki-os.org} does not experience these problems as their \ac{DCO} calibration algorithm is different from TinyOS. We did not test this, however.

To not influence the operation of the rest of the microcontroller and since understanding the \ac{DCO} calibration algorithm is not the focus of this thesis, we chose not to correct \ac{DCO} drift directly, but counteract only its effect on baudrate.
To stay within the required tolerance of $\pm5\%$ relative error, we created a fixed lookup-table of ``inverse'' correction baudrates for 115.2kBaud as shown in Figure~\ref{fig:baudrate_look_up}.

Since calculation of prescaler values at runtime is very costly (requiring floating point arithmetic in a recursive algorithm) the look-up table only contains precalculated values, which are then copied into the registers at runtime.
The on-board sensor provides temperature to the \ac{UART} module, which then selects new prescaler values from the look-up table for every \SI{5}{\celsius} temperature difference, which shows up as a sawtooth pattern in Figure~\ref{fig:baudrate_look_up_error} of the resulting relative error of the corrected baudrate.

We used this correction table without change on all of our motes and did not encounter this problem again.
This shows that even with slight differences in clock drift coefficient between different motes, this is approach is enough to solve this issue for our study.

Clock drift is not an issue for the communication between the MSP430 and the CC2420, as it is connected via the \ac{SPI}, which is a synchronous master-slave bus that provides the communication clock for its slaves, requiring no synchronisation on data symbols.

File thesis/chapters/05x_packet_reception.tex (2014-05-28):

\section{Packet Reception Rate}
\label{sec:packet_reception_rate}

The effect of temperature and other environmental factors on link quality has most thoroughly been investigated with the conclusion that all measurements of link quality deteriorate with higher temperature, as one would expect~\cite{Wennerstrom2013, Boano2013, Boano2014, Zuniga2013}.
However, Boano~\etal{} showed in their experiments that this behavior is not symmetrical, since heating the transmitter caused a more significant drop in \ac{PRR} than heating the receiver~\cite{Boano2013}.

In this experiment we used the same physical setup as described in Section~\ref{subsec:effects_of_temperature}, but with random payload as message content.
We fixed mote rotation to create a link that is just starting to deteriorate at \SI{50}{\celsius}, so that at low temperatures the link is of good quality, while at very high temperatures the link will experience high \ac{BER}s.

We increased the temperature of the mote in box 0 in steps of \SI{5}{\celsius} and \SI{10}{\celsius} up to \SI{80}{\celsius} and kept the mote on box 1 at constant \SI{30}{\celsius}, while sending 180.000 messages back and forth.
Then we repeated this, but heated box 1 and kept box 0 temperature constant.
To cancel out environmental factors we ran this experiment four times over two days, so we could then pick the two results with the least interference.

For the evaluation we plotted the normalized \ac{PRR} of messages sent from one mote and received by the other mote over temperature and time and included \ac{BER} and \ac{LQI} and \ac{RSSI} values to illustrate link quality.
Figure~\ref{fig:prr_link_01} shows messages sent from mote 0 addressed to mote 1 for both temperature cycles, while Figure~\ref{fig:prr_link_10} shows the opposite direction.
It becomes immediately clear that a higher temperature of either transmitter or receiver makes the link quality worse, validating the findings of Boano~\etal{} and Wennerstr{\"o}m~\etal~\cite{Boano2013, Wennerstrom2013}.
However, this relationship is neither linear nor symmetrical.

\subsection{Effects of Temperature on \acs{PRR} and \acs{BER}}

In Figure~\ref{fig:prr_link_01} the decrease in \ac{PRR} is small and relatively symmetrical up to about \SI{65}{\celsius}, however, past that point we see a dramatic change, with the increments in temperature translating very strongly into significant drops in \ac{PRR}.
The drop in \ac{PRR} is not symmetrical and becomes much more pronounced, when the receiver is heated than when the transmitter is heated, especially visible in the last increment from \SI{70}{\celsius} to \SI{80}{\celsius}.

This asymmetry is even more extreme in link 1-0, shown in Figure~\ref{fig:prr_link_10}, where heating the receiver beyond \SI{70}{\celsius} will cause an almost complete loss of message reception.
Interesting is the little dip in \ac{PRR} around \SI{50}{\celsius} in Figure~\ref{fig:prr_link_10_receiver}, which was present in this link in all four experiments with varying intensity. We suspect that this is a non-linearity in the radio, cases of which have also been reported by Boano~\etal

The \ac{BER} acts like an inverse function of \ac{PRR}, since higher \ac{BER} yields more messages with at least one bit error.
Noise on \ac{PRR} is visible in the standard deviation of \ac{BER} as exemplified by Figure~\ref{fig:prr_link_10_transmitter}.

\subsection{Effects of Temperature on \acs{LQI} and \acs{RSSI}}

The \ac{LQI} is a very good mirror of the \ac{PRR} of messages without error.
When the receiver is kept at a constant temperature, the values decrease almost linearly with temperature of the transmitter.
This is not the case when the receiver is heated, where a linear correlation to temperature , but is still very similar to the behavior of \ac{PRR}.
We therefore can confirm that \ac{LQI} is a good source for an estimate on \ac{PRR}.

This is very much not the case with \ac{RSSI}, which has much lower resolution that \ac{LQI} and exhibits hysteresis and non-linearities~\cite{Boano2013}.
While in Figure~\ref{fig:prr_link_01}, \ac{RSSI} ends up being lower when the receiver is heated than when it is constant, Figure~\ref{fig:prr_link_10} shows very similar values, even though \ac{PRR} is radically different.

It is also noteworthy that contrary to \ac{LQI}, \ac{RSSI} attempts to describe signal strength (\ie the power level being received by the antenna), which of course does not change, when the transmitter is at constant temperature.
Therefore, without temperature information, the \ac{RSSI} value is misleading, since it represents the power level not at the antenna, but at the signal amplifying stage of the radio. 
Therefore \ac{RSSI} is usable for a very inaccurate estimate of link quality at best, with little to no difference between receiver and transmitter temperature.

\subsection{Discussion}

Our data strongly implicates the receiver as being more vulnerable than the transmitter to an increase in temperature, especially above \SI{65}{\celsius}.
These results are very much incompatible with the findings of Boano~\etal~\cite{Boano2013}, which is surprising since the only two differences between our experiment and theirs is the temperature range and the additional usage of the CC2520~\cite{cc2520} radio, which is very similar to the CC2420~\cite{cc2420}.
However, these differences should not account for completely opposing results.

Research by Bannister~\etal~\cite{Bannister2008} saw an asymmetry in output and received input power when heating transmitter and receiver separately.
At the same time, they measured \ac{PER} and found that above \SI{-90}{\dBm} \ac{RSSI}, temperature had little to no influence, while below that \ac{RSSI} value, \ac{PER} increased.
The authors concluded that the CC2420 \acl{LNA} stage is less efficient at high temperature, which would manifest itself in a significant increase in \ac{PER} (or a \emph{decrease} in error-free \ac{PRR}) on the receiver.
However, the \ac{RSSI} behavior in Figure~\ref{fig:prr_link_10} does not reflect a general truth of the results by Bannister~\etal{} and furthermore suggests no direct correlation between \ac{RSSI} and \ac{PRR}.

We noticed a strong focus in such research on understanding the impact of temperature on output and input signal power, however, it seems that \ac{RSSI} does not actually correspond to link quality in general.
From our data, a combination of \ac{LQI} and temperature seems to have the best correlation to \ac{PRR}, therefore we want to examine how we can use temperature to improve \ac{PRR} in these conditions.

\begin{figure}[t]
	\subfigure[Constant receiver, increasing \newline transmitter temperature.] {
		
		\label{fig:prr_link_01_transmitter}
	}
	\subfigure[Increasing receiver, constant \newline transmitter temperature.] {
		
		\label{fig:prr_link_01_receiver}
	}
	\caption{\acs{PRR} and link quality of messages received by mote \textbf{1} vs. temperature. For transmitter temperature see Figure~\ref{fig:prr_link_10}.}
	\label{fig:prr_link_01}
\end{figure}

\begin{figure}[t]
	\subfigure[Increasing receiver, constant \newline transmitter temperature.] {
		
		\label{fig:prr_link_10_receiver}
	}
	\subfigure[Constant receiver, increasing \newline transmitter temperature.] {
		
		\label{fig:prr_link_10_transmitter}
	}
	\caption{\acs{PRR} and link quality of messages received by mote \textbf{0} vs. temperature.  For transmitter temperature see Figure~\ref{fig:prr_link_01}. The asymmetry in \acs{PRR} shows much more clearly here.}
	\label{fig:prr_link_10}
\end{figure}

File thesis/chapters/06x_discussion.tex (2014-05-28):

\section{Discussion}

Considering that the goal of using an \ac{FEC} in the context of low power networks such as \ac{WSN}s is to maximize energy efficiency of communications, we are not only looking for the $k$ with maximum throughput, but also with the least retransmissions.
We also have to consider that the link quality can already be poor at low temperature, therefore using no parity bytes at low temperatures is not a good idea either.

As per our findings, we propose one possible \ac{RS} scheme starting with $k=70$, which is 12.5\% overhead (the same as the popular $RS(255,223)$~\cite{Ma2009}), at low temperatures and linearly increase this to $k=60$ (or 25\% overhead) as receiver temperature increases to $70\,^{\circ}\mathrm{C}$ and above.
Starting with $k=70$ will give some protection against a random decrease in link quality as seen in Figure~\ref{fig:throughput_link_01_receiver_fec}.
In cases of extremely high bit error, such as in Figure~\ref{fig:throughput_link_10_receiver_fec}, we can still regain some throughput by using $60-80\%$ coding overhead with $k=30$ or $k=20$.
However, considering the extremely low \ac{PRR} in this area (compare with Figure~\ref{fig:prr_link_10_receiver_fec}), most of these messages will likely never be received anyway, which makes this option only viable when communication at these temperatures is absolutely necessary.

The results of Boano~\etal~\cite{Boano2013} strongly suggested that the loss in \ac{PRR} is more pronounced when heating the transmitter than the receiver.
This would have allowed us to use local temperature measurements to adapt the coding strength of our \ac{FEC} scheme to counteract the loss in \ac{PRR}.
Unfortunately, our results firmly oppose the findings of Boano~\etal{}: heating the receiver creates a higher loss in \ac{PRR} than heating the transmitter, therefore making such an approach unusable.
However, using temperature as another source for assessing link quality has the distinct advantage of being always available on the receiver locally, compared to \ac{LQI} and \ac{RSSI}, which requires a message to be received first.

We therefore propose another solution to adapt \ac{FEC} strength:
the receiver should monitor its local temperature and send out a warning broadcast to all potential transmitters, before its temperature becomes too high.
The transmitters can then address this mote with the appropriate \ac{FEC} strength.
The advantage of this active, preemptive approach over backchanneling link quality information is that in setups where transmissions only occur sparsely, a ``test'' transmission to judge link quality is not required.

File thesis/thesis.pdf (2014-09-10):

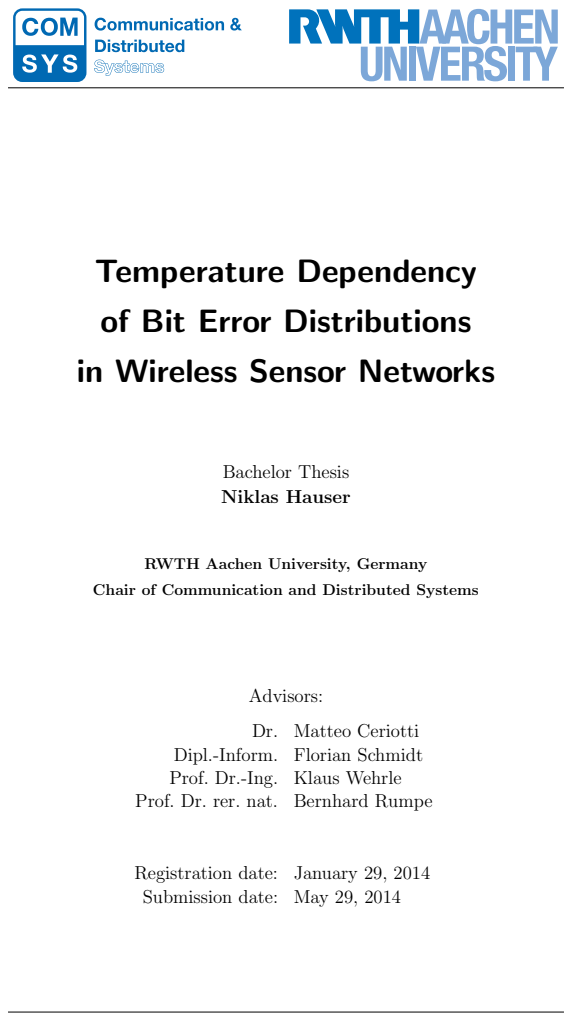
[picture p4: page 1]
Bachelor Thesis; Niklas Hauser; Advisors:

Temperature Dependency
of Bit Error Distributions
in Wireless Sensor Networks

RWTH Aachen University, Germany

Chair of Communication and Distributed Systems

Dr. Matteo Ceriotti

Dipl.-Inform. Florian Schmidt
Prof. Dr.-Ing. Klaus Wehrle
Prof. Dr. rer. nat. Bernhard Rumpe

Registration date: January 29, 2014
Submission date: May 29, 2014

I hereby affirm that I composed this work independently and used no other than the specified sources and tools and that I marked all quotes as such.

Hiermit versichere ich, dass ich die Arbeit selbstst¨andig verfasst und keine anderen als die angegebenen Quellen und Hilfsmittel benutzt sowie Zitate kenntlich gemacht habe.

Aachen, den 29. Mai 2014

Kurzfassung

Mit der Verfugbarkeit von leistungsf ¨ | ¨ahigen eingebetteten Ger¨aten und kostengun- ¨
stigen Funkmodulen, beginnen auch immer mehr batteriebetriebene Sensorger¨ate miteinander zu reden und Probleme gemeinsam zu entscheiden. Es ist abzusehen, dass die Benutzung solcher intelligenten Ger¨ate in drahtlosen Sensornetzwerken industrielle Prozesse vereinfachen und unsere Lebensqualit¨at verbessern wird.

Allerdings ist die Laufzeit dieser mobilen Ger¨ate durch ihre endliche Energiequelle, die meist nur mit viel Aufwand zu wechseln ist, beschr¨ankt. Daher braucht es eine Programmierung, die energiebewusst kommuniziert, um die Lebensdauer der Batterie so weit wie m¨oglich zu verl¨angern. Drahtlose Kommunikation ist stark durch Umweltver¨anderungen, allen voran die Lufttemperatur, beinflussbar, was zu Korruption oder Verlust von Paketen fuhren kann und ein erneutes Versenden des Pakets ¨ nach sich zieht.

In dieser Arbeit beschreiben wir eine kostengunstige Testplatform zum Testen der ¨ Funkverbindungen in einer temperaturkontrollierten Umgebung. Mit dieser Platform untersuchen wir die Empfangsraten und die Bitfehlerverteilungen in korrupten
Paketen. Unsere Ergebnisse widerlegen fruhere ver ¨ | ¨offentlichte Ergebnisse. Schließ-
lich wenden wir diese Erkenntnisse auf die Programmierung eines Simulators an, mit dem wir untersuchen, wie sich Temperatur als Eingabegr¨oße einer adaptiven Vorw¨artsfehlerkorrektur verh¨alt, um damit die Empfangsraten korrupter Pakete zu verringern.

Abstract

With the availability of powerful embedded devices and inexpensive radio communication, ever more battery powered sensor devices make use of the added connectivity to talk to each other and decide problems collectively. It is envisioned that usage of such smart devices in Wireless Sensor Networks will streamline industrial processes as well as improve our quality of life.

However, the runtime of these mobile devices is limited by their finite power source, which most often are impractical to exchange. Therefore energy-aware programming and communication is required to prolong battery life for as long as possible. Unfortunately, wireless communication is strongly influenced by environmental changes, most prominently air temperature, which can lead to packet corruption or loss and requires energy-consuming retransmissions.

In this work we describe a low-cost testbed for testing radio performance in a temperature-controlled environment, with which we examine packet reception rates and bit error distributions within packet corruption. Our results disprove previous published findings. Finally, we apply these findings on building a simulator, with which we investigate using temperature as an input for an adaptive Forward Error Correction scheme to improve packet reception rates and thereby reduce unnecessary retransmissions.

# Acknowledgments

I want to thank my advisors Matteo and Florian for their time and support. Our discussions kept me focused on what was important and constantly pushed me towards improving the experiments and evaluations.

Many thanks go to my supervisor Prof. Dr.-Ing. Klaus Wehrle and to my second supervisor Prof. Dr. Rumpe.

My parents deserve my gratitude many times over for their never ending love and support.

# Contents

1 Introduction | 1
2 Background | 3
3 Related Work | 7
4 Testbed Description | 11
5 Experiment Results | 17

6 Forward Error Correction | 29
7 Conclusion | 39
Bibliography | 41
A Appendix | 45

1

# Introduction

With the introduction of more powerful low-power embedded devices, such as small microcontrollers, and the increased availability of low-cost radio transceivers especially in the last decade, more and more applications have been developed that enrich their functionality by receiving input from our environments. Such applications can help us to use natural resources, such as farm land or forests, more efficiently, or streamline industrial processes by retrofitting more data sampling points, or simply alarm us when we forget to water the plants at home.

Concepts of augmenting our environments with connected sensors and actuators have been talked about for many years, with the most prominent concept being the Internet of Things (IoT). Here everyday objects are able to communicate with each other over local networks or the Internet and come to smart decisions collectively. This infusion of information about the real into the virtual world will keep growing with many new and exciting ways to improve our quality of life.

However, these concepts are built on very new technology, which has to be understood to be improved for the next generation of such devices. The common culprit of today’s mobile devices are their battery lives. Even though impressive advancements have been made, especially in the area of smart phones, charging or exchanging batteries is cumbersome at best, and, in regard to sensor devices, impractical when they are distributed over large areas. It is therefore imperative to extend battery life for as long as possible, which means not only using low-power hardware, but also merging it with energy-efficient software.

Fortunately, long and intensive computations do not have to be performed on the sensor devices locally, but can be delegated to a server connected to the power grid. For that however, the sensor nodes must communicate using radio communication, which is by the laws of physics and electrical engineering still inherently energyinefficient, especially compared to wired communication.

What sounds simple actually is complicated by the fact that radio communication is at the mercy of the environment, which introduces noise into the signal and

2 | 1. Introduction

strongly influences signal propagation. Further complications arise with different antenna designs, the limitations of the modulation scheme and non-linearities in analog circuitry. This leads to packets being corrupted or not being received at all, requiring the retransmissions of the original packet until it is received error-free. However, in conditions of poor link quality this might not even be possible. Hence, to reduce energy consumption, radio communication, especially retransmissions, must be kept to a minimum while not impairing functionality of the original application.

Additionally, a typical Wireless Sensor Network is deployed outside and its nodes are protected by air-tight containers from precipitation. On a sunny day, temperatures inside these containers can climb well above outside air temperature, which influence radio and microcontroller performance quite dramatically. In this thesis we focus on what impact temperature has on patterns in packet corruption and describe the experiments we created to study these patterns. We analyze the results and try to improve link quality using Forward Error Correction.

The main contributions of this thesis are:

1. the creation of a low-cost testbed for testing radio performance in a temperature-controlled environment (Chapter 4),
2. the investigation of microcontroller clock drift, and the limitations of its calibaration in TinyOS (Chapter 5),
3. the detailed analysis of the effects of temperature on bit error patterns and
| Packet Reception Rate, which disproves published findings by Boano et al. [6]
(Chapter 5),
4. the modeling of the discovered patterns using a simulator (Chapter 6), and
5. the investigation of using an adaptive Forward Error Correction scheme to
| improve throughput in temperature-influenced link conditions (Chapter 6).

We provide the necessary background knowledge required for understanding our work in in Chapter 2, before briefly discussing previous, related work in Chapter 3.

2

# Background

This work centers around investigating and improving the quality of corrupted communications in low power networks. Therefore this chapter will provide the necessary background information on the form of communication used in Wireless Sensor Networks and the radio and microcontroller hardware we employed in our study. Furthermore, we shortly describe what approaches to Error-Correction Codes exist and how they work.

## 2.1 Wireless Sensor Networks

A Wireless Sensor Network (WSN) comprises of two or more nodes, called motes, which can communicate using low power radio communication. This provides a means to easily deploy sensing, actuating and communication infrastructures in a given space. The nodes are mostly powered by small and simple microcontrollers connected to a radio and other peripherals such as sensors and actuators as shown in Figure 2.1.

Networked motes communicate with their neighboring motes and can address the whole network via multi-hop transmissions, therefore deprecating the use of expensive wired buses. However, due to the nature of wireless communication, the software must be built to tolerate unreliable communication links, which can change network topology and result in high latency in data exchanges or a complete loss of communication.

Integrated batteries are used to power the motes for a certain amount of time when deployed in areas where access to a power grid is too costly or impossible. Especially for these battery powered applications, conserving energy is a high priority and places tight restrictions on the type of CPU and radio transmission power and duty cycle, effectively limiting communication range and bandwidth.

4 | 2. Background

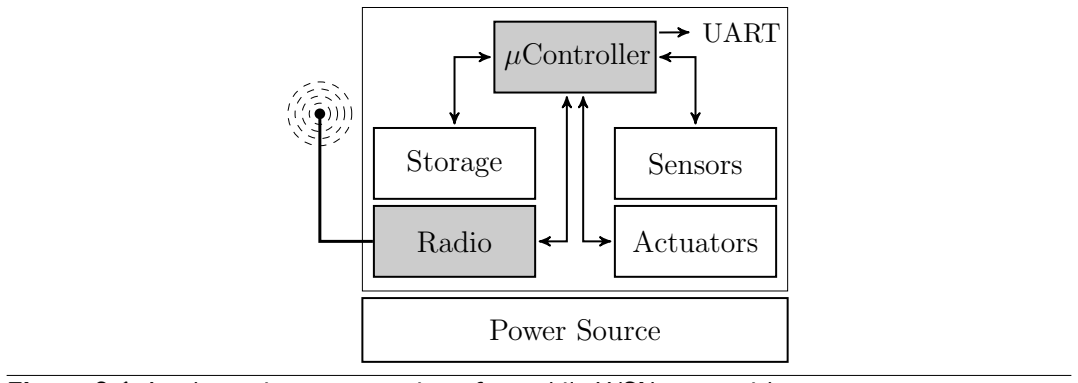
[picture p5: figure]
µController; Sensors; Radio; Actuators; Storage; UART; Power Source

Figure 2.1 A schematic representation of a mobile WSN mote with a power source.

A typical application for a WSN would be the collection of meteorological information over large inaccessible areas, such as forests, or the monitoring of large industrial complexes to reduce the cost of wiring [4]. The high effort required to exchange empty batteries in these scenarios demands energy-aware programming, which keeps the overall energy consumption to a minimum.

## 2.2 Communications

Since this works focuses heavily on communications between motes, we use specific terms to help describe its properties.

A packet is the basic unit of communication between two motes, containing metadata, such as sender and addressee, and payload. A message is the interpretation of the payload of one or several packets. If a message is very long, it might be fragmented into several packets, however, in all our experiments, one message uses only one packet. We define a link as the transmission of messages from one mote addressed to another over a period of time, even when none of these messages where received by the addressee, due to channel effects or connection problems.

### 2.2.1 IEEE 802.15.4 Standard

In this work we use the CC2420 wireless transceiver [22], a very common communication radio in WSNs. The CC2420 implements the Institute of Electrical and Electronics Engineers (IEEE) 802.15.4 standard and uses Offset QPSK (OQPSK) modulation in the 2.4 GHz ISM band with a nominal data rate of 250 kbit/s.

The Physical Protocol Data Unit (PPDU) is the lowest accessible layer as shown in Figure 2.2 with a maximum size of 133 bytes. This leaves 127 bytes for the MAC Protocol Data Unit (MPDU) and between 102 and 122 bytes for the frame payload. To increase robustness of transmission, each byte is split into two 4-bit symbols, which are then mapped to a 32-bit chip sequence and modulated using OQPSK.

These 32-bit chip sequences are part of IEEE 802.15.4 and were chosen to produce high Hamming distances against each other, so that bit errors can already be corrected within the received chip sequence to some degree. The higher the Hamming

2.2. Communications | 5

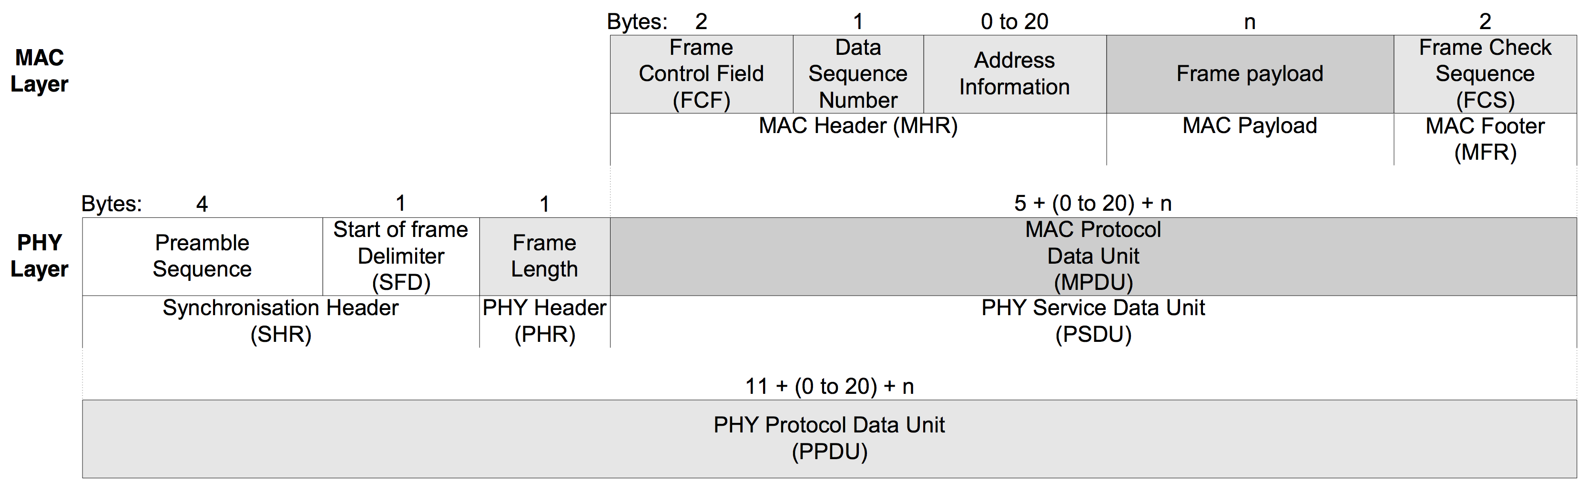
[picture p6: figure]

Figure 2.2 The packet format implemented defined by IEEE 802.15.4 taken from [22].

distance between two sequences, the less likely they are to be mistaken for one another. Therefore a corrupted 4-bit symbol is only received, when a corrupted chip sequence is mistaken for another sequence, which requires several bits of the 32-bit sequence to be flipped. The minimum Hamming distance between two sequences is 12 bit, the maximum is 20 bit [20].

At the beginning of every transmission, a Preamble Sequence is modulated, which triggers a listening mote to synchronize and receive this new packet. Typical reasons for not receiving packets are either the reception of a signal with too little power to be noticeable above the channel noise, or the reception of a corrupted preamble, so that the listening mote does not start receiving a packet, even though the power levels would permit it.

When a packet is received, its Frame Check Sequence (FCS) is automatically evaluated to check for bit errors introduced by channel noise. However, a failed FCS test can also be the results of a corrupted Frame Length field. This prompts the radio to read in too few or too many bytes, thereby comparing the FCS results to the wrong bytes at, what the receiver wrongly considers the “end” of the packet.

Even though the FCS is evaluated for all messages automatically, the CC2420 allows retrieval of corrupted messages, including all hardware link qualifiers such as Link Quality Indication (LQI) and Received Signal Strength Indication (RSSI). We make use of this ability to analyze the content of these corrupted messages in our work.

### 2.2.2 UART Communication

The microcontroller can also communicate over a wired bus using its Universal Asynchronous Receiver Transmitter (UART) module. UART does not provide a seperate clock line (hence asynchronous), which requires the receiver to synchronize itself at the beginning of each symbol transfer and sample the signal at multiples of the baudtime tsymbol = fClock/fBaudRate, which derives from the baudrate of the transmitter. Here the receiver synchronizes on the falling edge of the start bit, which is always low, and has to sample the successive bits at the just right time, as shown in Figure 2.3. If the transmitter’s and/or receiver’s clock is running too slow or too fast, then tSymbol is too small or too large, resulting in a corrupted sampling of the bits in the symbol as marked in red.

6 | 2. Background

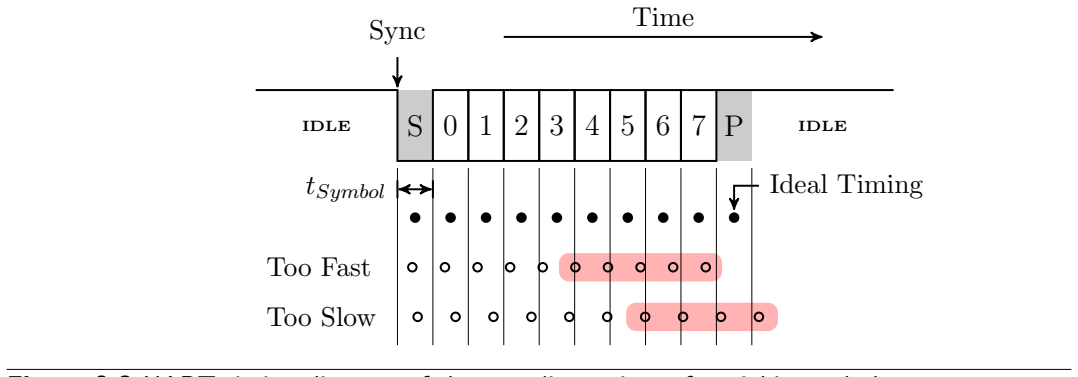
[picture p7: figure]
IDLE; Time Sync; tSymbol; Ideal Timing; Too Fast; Too Slow

Figure 2.3 UART timing diagram of the sampling points of an 8-bit symbol.

The relative error tolerance for the 8N1 configuration shown in the Figure (8 databits, 1 startbit and 1 stopbit) is ±5%, since the sample point of the stop bit may only shift by at most ±tSymbol/2. With 10 bits to read, one tSymbol equals one tenth of the symbol transmission time, hence a relative tolerance of ±5%. For example, the tolerance for 7-bit transfers (9 baudtimes) increases to ±5.56%.

However, since both transmitter and receiver may experience clock drift, the error must not exceed 5% in total, which in the worst case of opposing clock drift directions (one too fast, one too slow) imposes a tight allowed deviation of +2.5% and −2.5% on the modules respectively. In practice, UART can therefore be difficult to use with uncorrected or unknown clock drifts.

## 2.3 Error Control Schemes

There exist two approaches to improve the quality of an imperfect communication channel: using Forward Error Correction (FEC) to add redundancy before transmission, so that bit errors can be detected and corrected by the receiver, and using Automatic Repeat Query (ARQ) to only detect bit errors, but request a retransmission, instead of correcting them. While ARQ is simple and requires very little computational and transmission overhead, it does perform poorly in conditions with a high channel error rate. FEC allows constant throughput at the expense of coding and decoding time and transmission overhead, depending on the specific Error-Correction Code (ECC) used. To overcome their individual disadvantages, these two approaches can be merged into hybrid ARQ schemes, however, in our work we will be focusing on using FEC schemes alone.

The simplest ECCs belong to the class of linear cyclic coding schemes, where a bit stream is divided into non-overlapping blocks, which are then encoded separately. The most widely used linear cyclic block codes are binary Bose-Chaudhuri-Hocquenghem (BCH) and non-binary Reed-Solomon (RS) codes, both of which can be used to correct bit and burst errors. There are several other approaches to ECCs, however, they go above the focus of this work.

3

# Related Work

The research field of investigating influences of the environment on wireless link quality is large and spans many technologies and protocols. However, we focus on technologies deployed in low power networks such as WSNs, where the advances in small and affordable radio technology pushed research forward. In a first step towards energy efficient, reliable communications, especially in battery powered applications, a deep understanding of why messages become corrupted is required.

Here we present research relating to the IEEE 802.15.4 protocol used in most WSNs, especially in the three areas this work focuses on, namely, the influence of temperature on link quality and bit error distributions within corrupted messages, as well as the use of FEC to counteract these effects.

## 3.1 Effects of Temperature

Bannister et al. [3] were one of the first to systematically investigate the effect of temperature on the performance of the CC2420 radio. They connected two radios together via coaxial cable with attenuators and placed one of them in a thermal chamber with a temperature range of 25 to 65 ◦C while measuring signal power using the RSSI. The results showed a reduction of output power by 4 − −5 dBm when the transmitter was heated, but only 3 dBm reduction in measured input power when the receiver was heated. Boano et al. [5] also investigated this behavior in 2010 in a real world deployment, but found no difference in RSSI between transmitter and receiver. However, both works point to a loss of gain in the CC2420 Low Noise Amplifier (LNA) as the source of the reduction in signal powers at higher temperatures.

In a long-term outdoor study in 2013, Wennerstr¨om et al. [26] examined the correlation between RSSI and Packet Reception Rate (PRR) and environmental factors, such as temperature, relative and absolute humidity, precipitation and sunlight.

8 | 3. Related Work

They found that of all environmental factors, temperature had the strongest influence, with an increase in temperature causing a significant decrease in both RSSI and PRR. This was further researched by Boano et al. [6], who focused on the impact of temperature on RSSI, Signal-to-Noise Ratio (SNR), Noise Floor, PRR and LQI. They determined a negative impact of temperature on all these values and expanded their work by looking at the asymmetry of PRR when heating the transmitter and receiver. They found that the loss in PRR was more pronounced when heating the transmitter than the receiver.

Finally, Z´u˜niga et al. [25] created a summarizing report on the effect of environment variables on current WSN motes. Apart from including all previous findings, they also describe a substantial negative impact of temperature on microcontroller clock drift. However, the CC2420 clock is compensated for temperature and experiences no such drift.

## 3.2 Bit Error Distributions

Liang et al. [14] investigated bit error distributions in the context of 802.11 (WiFi) interference. They found that packet collisions cause burst errors, due to 802.11 packets typically being much shorter than 802.15.4 packets, particularly in the beginning of a message. This is due to the 802.11 sender deferring sending its packets until the 802.15.4 transmission completed, however only if the 802.15.4 sender is close enough so that its transmission power can be sensed by the 802.11 collision avoidance algorithm. If the 802.11 sender cannot sense the 802.15.4 transmission, the authors show an even bit error distribution across the entire packet.

Schmidt et al. [20] examined the bit error distributions within corrupted messages in their outdoor testbed of 20 TelosB devices. Similar to Liang et al., they found that for random payload, Bit Error Rate (BER) remains stable throughout message, however, within all 4-bit symbols, the Most Significant Bit (MSB) is significantly less likely to break than the 3 Least Significant Bit (LSB). In addition, symbols with MSB set to 1 are more likely to break than symbols with MSB set to 0. This behavior creates very different Hamming distances between the broken symbols coded in 32-bit chip sequences than defined by the 802.15.4 standard. The authors also looked at burst error distribution and found these errors not independently distributed, but skewed towards longer bursts.

Their findings then where further completed by Hermans et al. [12] with an understanding of why the Hamming distances are different than expected. The authors discovered that the pattern fits, when their simulation of these patterns uses a Minimum Shift Keying (MSK) instead of the OQPSK demodulator suggested by the 802.15.4 standard. The MSK demodulator can correctly receive packets sent by an OQPSK modulator, but it outputs different code words than defined by the standard. The authors hypothesized that these code words then have to be translated using a table, which would create the distinct bit error patterns.

3.3. Forward Error Correction | 9

## 3.3 Forward Error Correction

The use of FEC schemes in communication has been investigated before, however, the available limited resources on WSN motes focus research in this area very much on coding and energy efficiency.

Jeong et al. [13] investigated the performance of single- and double-bit correcting ECC on very early WSN motes, not using the 802.15.4 standard. They came to the conclusion, that using BCH codes is simple to implement, but performs poorly when encountering burst errors. Busse et al. [8] then compared the performance of a Hamming code, an interleaved double-bit correction code and a RS code using their WSN and found the RS code to be the most efficient of them, both in the length of the added overhead, as well as the error correction capabilities.

Using mathematical energy consumption modeling, Tian et al. [23] showed that for small packet lengths (< 1023 bytes) BCH codes outperform ARQ. However, research by Ma et al. [16] points to RS being more energy efficient than BCH codes, especially when considering the energy consumption of transmitting the coding overhead.

Ahn et al. [1] examined changing FEC coding strength dynamically based on link quality properties. Their adaptive FEC algorithm outperformed several static RS codes in simulation, as well as in real traces. Liang et al. [14] created and evaluated an efficient, TinyOS compatible RS implementation, called TinyRS, during their research on bit error distributions mentioned before.

10 | 3. Related Work

4

# Testbed Description

In order to be able to investigate the effects of temperature on our WSN motes, we built a new low-cost testbed, which can accurately control mote temperature and allows the mote to maintain a certain antenna position. Furthermore, we wrote flexible control and evaluation software, which orchestrates the experiments and logs all relevant data to disk. In this chapter we will describe the design decisions we made and how they influence the testbed performance.

## 4.1 Temperature Box

For our experiments we needed a way to accurately control temperature of motes in our WSN. Even though previous setups used an infrared lamp [7, 11] to heat the motes directly, we chose to control mote temperature only using air temperature. The mote is placed in a closed Polystyrene (PS) hard-foam box and the confined air is heated to the requested temperature and circulated to transfer this heat to the mote. The box has the outside dimensions of 35 cm × 35 cm × 30 cm with a wall thickness of 5 cm which results in a holding capacity of 12.5 l.

### 4.1.1 Hardware

A microcontroller evaluates temperature sensors within the box and locally controls the duty cycles of a small fan and a 150W ceramic heating element using a closed-loop PID controller to achieve the requested air temperature. The microcontroller can communicate over a serial connection to receive the desired temperature and send the current temperature.

Additionally, air temperature is displayed as a hue from blue (cold) via green (warm) to red (hot) on a RGB LED. The duty cycles of the heating element and fan are mapped to two white LEDs, to provide an immediate status overview and prevent burn injuries.

12 | 4. Testbed Description


Figure 4.1 Baseplate with temperature controller, heating element, fan and sensor mote.

The box is powered by a 300W PC power supply, which was chosen for its ability to provide 12 V, 5 V and 3.3 V at the required currents, which removes the need for additional (costly) voltage conversion. A custom designed PCB distributes power from the ATX connectors to two high and two medium power MOSFET switches and up to five temperature sensors, all controlled by an ATmega328.

The PCB, heating element and fan are fixed on a wooden baseplate shown in Figure 4.1 using custom fasteners and standard screws. All custom made parts were prototyped using the PCB mill and laser cutter of the RWTH FabLab [10].

### 4.1.2 Embedded Software

The embedded software is written in C++ using the xpcc microcontroller framework [27] and implemented as a set of asynchronous control tasks for input parsing and output formatting, temperature sensor evaluation, PID loop update and duty cycle generation. The choice of an ATmega328 as a microcontroller was deliberate to enable compatibility with the Arduino framework, which might be more familiar to developers.

Once the controller is programmed via In-System Programming (ISP), it will periodically send the values of all attached temperature sensors, as well as the current heating element power setting in human-readable ASCII format. Desired temperature can be sent as an ASCII formatted integer followed by the letter ‘C’. All

4.2. Mote Harness | 13

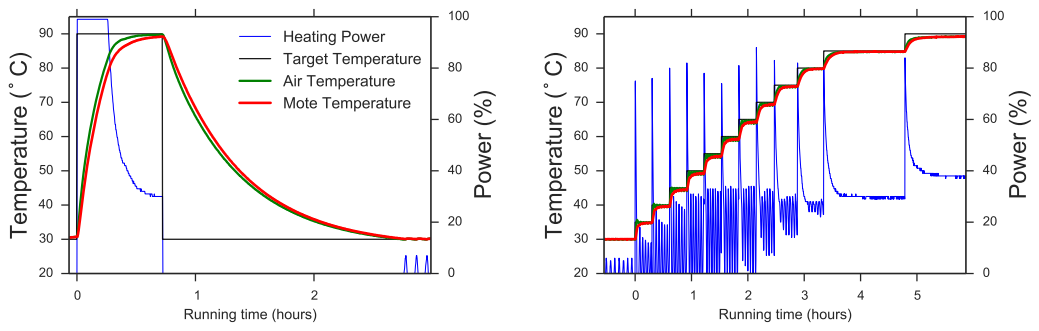
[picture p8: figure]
Power (%); Heating Power Target Temperature Air Temperature Mote Temperature; Running time (hours)

(a) Heating to 90 ◦C, then cooling to 30 ◦C.
(b) Temperature increments of 5 ◦C.

Figure 4.2 Typical performance of the boxes over time. Notice the mote temperature (red line) lagging behind air temperature (green line).

switching frequencies were kept well below 1 kHz to avoid any kind of interference with the 2.4 GHz band.

### 4.1.3 Performance

The heating element has enough power to heat the air inside the box up to 120 ◦C. This can however damage both the PS material as well as the mote, so a hard limit of 90 ◦C is imposed during experiments.

As seen in Figure 4.2(a) it takes about 40 minutes to heat up to 90 ◦C and about 2 hours to cool back down to 30 ◦C. The PID loop is deliberately dampened so that no overshoot in air temperature occurs, however, since the mote temperature naturally lags behind, a slight overshoot in air temperature might actually help achieve desired mote temperature quicker. However, during the experiments a more granular approach is used similar to Figure 4.2(b).

The boxes can be retrofitted with an active piezoelectric cooling element and a fan by connecting them to the two unused MOSFET switches on the controller and updating the software, which also allow reaching temperatures below room temperature. Since we did not use a cooling element, we set the minimum experiment temperature at 30 ◦C so that in a room temperature of 20−25 ◦C it can still be reached within reasonable time.

Compared to TempLab by Boano et al. [7], which uses infrared heat lamp controlled via the wireless Z-Wave home automation protocol, our boxes require more manual assembly, do not operate wirelessly and cannot change temperature as fast. However, our boxes also only cost one third as much (e 91 versus e 293).

## 4.2 Mote Harness

In order to guarantee that both sender and receiver will not move during experiments a mote harness was developed and laser cut out of acrylic. The mote snaps into the harness so that the axis of rotation goes through the middle of the PCB antenna

14 | 4. Testbed Description


(a) Harness with mote on a distance bar. | (b) Vector drawing of the rotation disc.

Figure 4.3 The mote harness allows precise positioning of motes.

which then allows rotation in 5◦
steps as shown in Figure 4.3. Furthermore, the distance between two harnesses can be adjusted in 5 mm steps using laser-cut wooden distance bars.

In our experiments this greatly improved the handling of the motes. Where before we used to tape the mote down into position, which was an inaccurate matter at best, we now have a simple and elegant solution. However, we ended up not actually using the distance bars in most of our experiments, as it was simpler to use antenna orientation to control link quality than distance. Therefore, in Figure 4.1 the mote harness is fixed onto the baseplate.
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

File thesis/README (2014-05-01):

To build this you have to clone the thesis-tex.git repository to some appropriate place.
For instance, put it in ~/.tex/tex/thesis-tex [see note_1] and set the environment variables:
  export TEXMFHOME="$HOME/.tex"
  export TEXINPUTS=".:$HOME/.tex:"                          # that's needed for latex
  export BSTINPUTS=".:$HOME/.tex/tex/thesis-tex/styles:"    # that's needed for bibtex
If you have more comsys templates checked out, this might be useful to you:
  export BSTINPUTS='.:'"$(ls -1d "$HOME"/.tex/tex/*/styles 2>/dev/null | tr '\n' ':')"

note_1: The /tex subdirectory is necessary for tex to find the right files. However, the $HOME/.tex part is abitrary. It defaults to $HOME/texmf and if you don't mind having a texmf directory in your home, you can put stuff there. In that case, you wont need to set TEXMFHOME,TEXINPUTS nor BSTINPUTS.

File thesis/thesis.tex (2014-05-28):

%% HEADER
%%%%%%%%%%%%%%%%%%%%%%%%%%%%%%%%%%%%%%%%%%%%%%%%%%%%%%%%%%%%%
\newcommand{\hyperrefpdfauthor}{}
\newcommand{\hyperrefpdftitle}{}
\newcommand{\hyperrefpdfsubject}{}
\newcommand{\hyperrefpdfkeywords}{}
\newcommand{\hyperrefpdfborder}{0}
\documentclass{wissdoc-kw-eng}

% \usepackage[german, english]{babel}
% \selectlanguage{english}

\newcommand{\eg}[0]{e.g., }
\newcommand{\ie}[0]{i.e., }
\newcommand{\etal}[0]{et~al.}
\newcommand{\floatwidth}[0]{\columnwidth}
\newcommand{\subfloatwidth}[0]{0.48\columnwidth}
\newcommand{\comment}[1]{}
\definecolor{Orange}{rgb}{1,0.5,0}

\newcommand{\todo}[1]{\textsf{\textbf{\textcolor{Orange}{[[#1]]}}}}

\usepackage{tikz}
\usetikzlibrary{decorations.pathmorphing,calc,shapes,shapes.geometric,patterns,snakes,matrix,arrows,positioning}

\usepackage{dcolumn}
\newcolumntype{d}[1]{D{.}{.}{#1}}
\usepackage{siunitx}
\DeclareSIUnit\dBm{dBm}

\usepackage[printonlyused]{acronym}
\renewcommand{\bflabel}[1]{\normalfont{\normalsize{#1}}\hfill} % keine serifenlose schrift für acronym
\usepackage{subfigure}

\usepackage{float}
\floatstyle{ruled}
\newfloat{listing}{htbp}{lop}[chapter]
\floatname{listing}{Listing}

\usepackage[hang,center,nooneline]{caption}
\captionsetup[figure]{font={small,sf}}
\captionsetup[table]{font={small,sf}}
\captionsetup[listing]{font={small,sf}}
\usepackage{etoolbox}
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

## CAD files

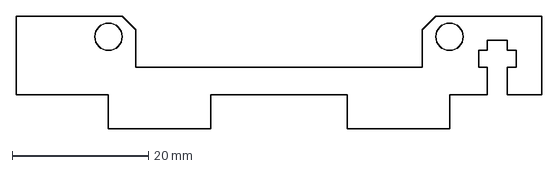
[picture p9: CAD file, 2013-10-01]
box/hardware/Fan_holder.dxf
77.0 x 16.5 mm

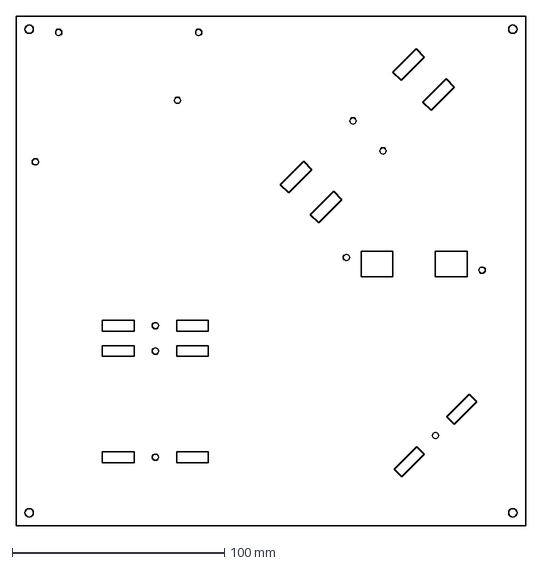
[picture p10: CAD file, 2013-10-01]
box/hardware/Baseboard.dxf
240.0 x 240.0 mm

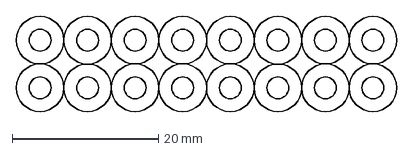
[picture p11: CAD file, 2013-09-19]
box/hardware/Distance_rings.dxf
52.0 x 13.0 mm

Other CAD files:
box/hardware/Heater_holder.dxf
position/mote_holder_5mm.dwg
position/length_connector_5mm.dwg
box/hardware/sensor_node_holder.dxf
position/rotate_bearing_5mm.dwg
position/length_bearing_6mm.dwg
box/hardware/wind_director.dxf
position/rotate_base_3mm.dwg
position/length_bearing_bottom_3mm.dwg
position/length_measure_5mm.dwg
position/rotate_wheel_4mm.dwg
position/rotate_bearing_3mm.dwg
box/hardware/Baseboard.dwg
box/hardware/Distance_rings.dwg
box/hardware/Fan_holder.dwg
box/hardware/Heater_holder.dwg
box/hardware/sensor_node_holder.dwg
box/hardware/wind_director.dwg

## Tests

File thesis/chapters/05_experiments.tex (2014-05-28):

\chapter{Experiment Results}
\label{chap:experiments}

This chapter describes the experiment setups we designed to focus on the effect of temperature on the mote hardware and link quality.
We present the evaluation of the experiment results and compare them to related work.

\section{Locations}

We executed these experiments in two locations: a temperature-controlled server room in a basement and a large empty storage space.
We chose these locations for their low visitation frequency, since the presence of moving objects, especially humans, alters the link quality, which of course was undesirable.

In the server room, a space of about \SI{3 x 12}{\metre} was available, with a thick load-bearing concrete wall on the one side and metallic server racks on the other.
This environment made for a very good link quality even at low power, which was the opposite of what we needed.
We tried a power setting of 3 (\SI{-25}{\dBm}), but even at the maximum attainable distance in the room the link was without bit errors, therefore we settled on power setting 2 (below \SI{-25}{\dBm}), which required the motes to be very close to each other at about \SI{30}{\centi\metre}.
Due to the difficulty of manipulating link quality with fine granularity, we only ran one experiment in this room and then relocated the setup.

The storage room was larger with about \SI{10 x 15}{\metre} and had a window front and many shelves on the walls.
Here we could use power setting 3 at about \SI{3}{\metre} distance and very accurately manipulate link quality.
Therefore we used this location for the remaining experiments.

\section{Desired Link Quality}
\label{sec:link_quality}

To create a link with the desired quality, we used a simple, live updated graphical display of \ac{LQI}, \ac{RSSI} and bit error values.
While links of intermediate quality are relatively easy to find, we found it difficult to find the right intermediate link quality with a high enough \ac{BER} for statistically significant results, but with also enough average message receptions, especially for a longer period of time.
These temporal characteristics have also been described by Baccour~\etal~\cite{Baccour2012}, specifically, that links of moderate average \ac{PRR} are less stable than with very low or very high \ac{PRR}.
Furthermore, the mere presence of a person in the same room as the motes caused a dramatic change in link quality, which has also been described by Baccour~\etal

We briefly considered using a controllable source of radio interference as proposed by Boano~\etal~\cite{Boano2009} to be able to make it easier to create the desired link qualities, however, its effect on the \ac{BER} patterns is unknown and we did not want to risk a corruption of our test results.
Therefore, finding and verifying the desired link quality with the acceptable amount of bit errors regularly took hours, especially when the motes where to be heated to different temperatures.
Even then, we had to repeat several experiments when link quality inexplicably changed.
An automated link quality ``creator'' using a motorized mote harness would certainly have helped.

All experiments were done using the on-board PCB antenna sending on channel 26, which is outside the allotted spectrum of 802.11, to minimize WiFi interference~\cite{Liang2010}.

\input{chapters/05x_clock_drift}

\input{chapters/05x_bit_patterns}

\input{chapters/05x_packet_reception}

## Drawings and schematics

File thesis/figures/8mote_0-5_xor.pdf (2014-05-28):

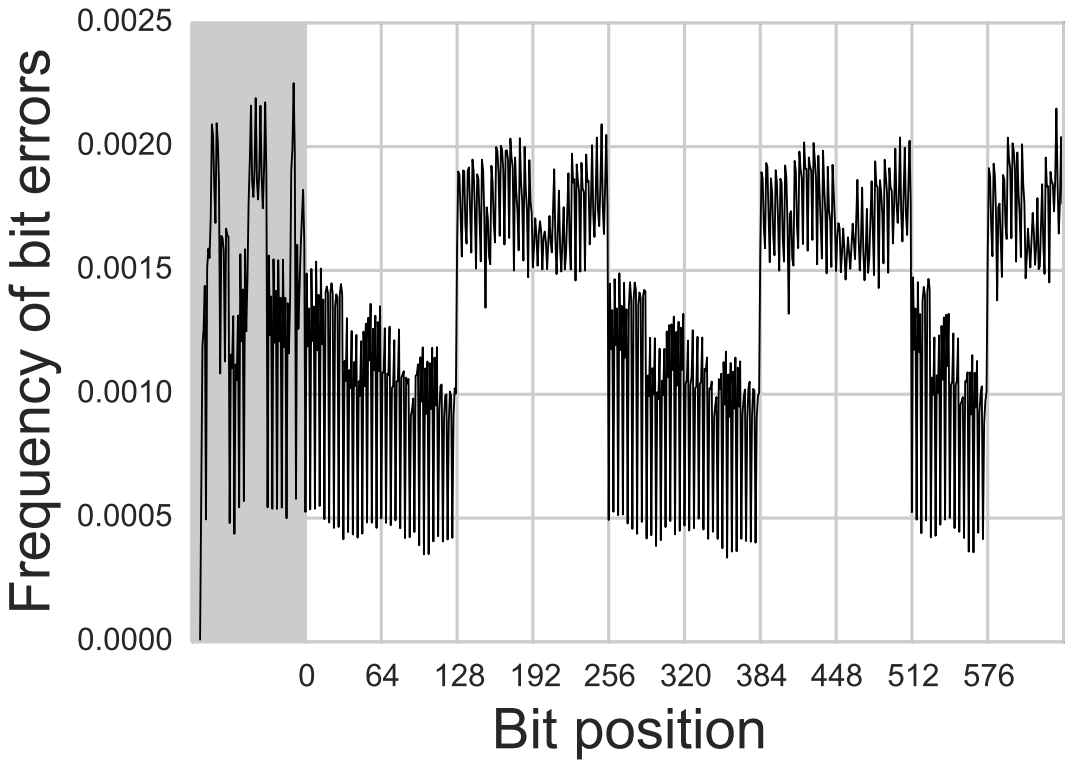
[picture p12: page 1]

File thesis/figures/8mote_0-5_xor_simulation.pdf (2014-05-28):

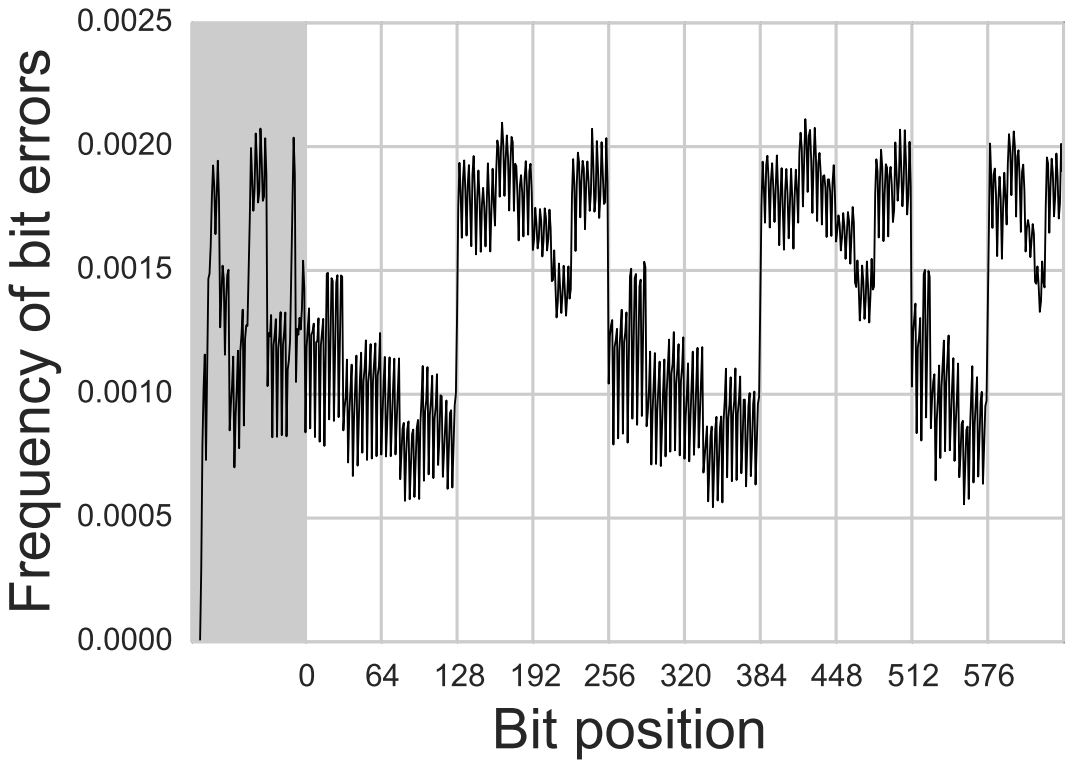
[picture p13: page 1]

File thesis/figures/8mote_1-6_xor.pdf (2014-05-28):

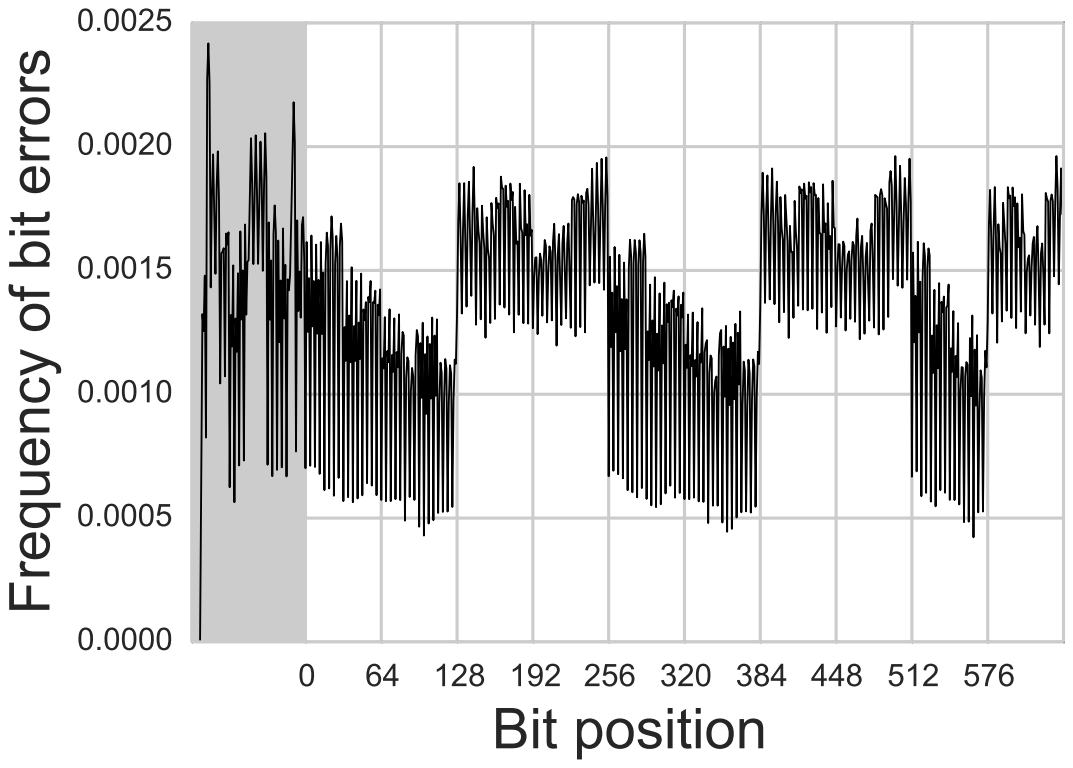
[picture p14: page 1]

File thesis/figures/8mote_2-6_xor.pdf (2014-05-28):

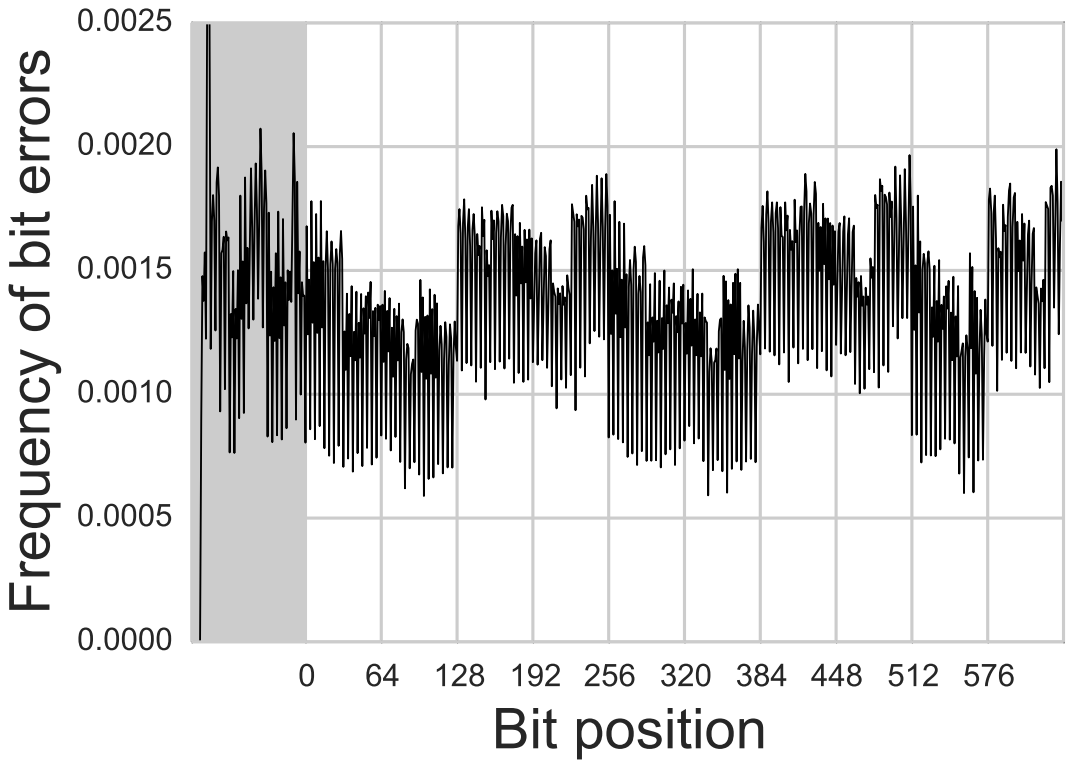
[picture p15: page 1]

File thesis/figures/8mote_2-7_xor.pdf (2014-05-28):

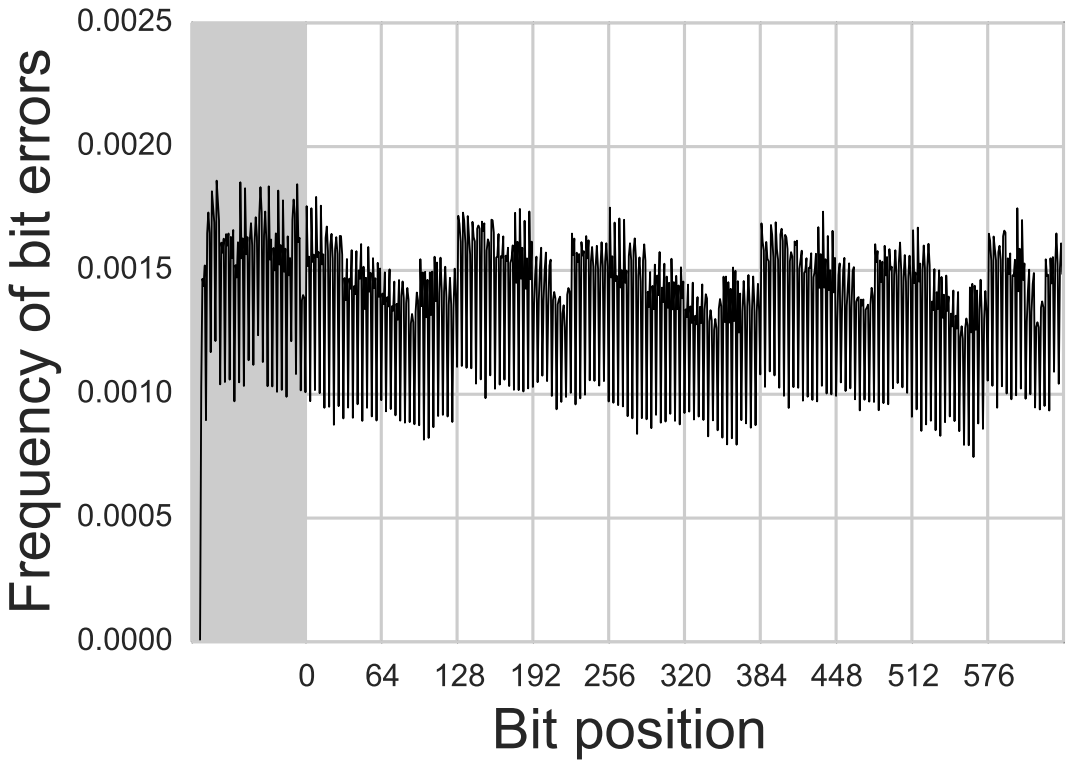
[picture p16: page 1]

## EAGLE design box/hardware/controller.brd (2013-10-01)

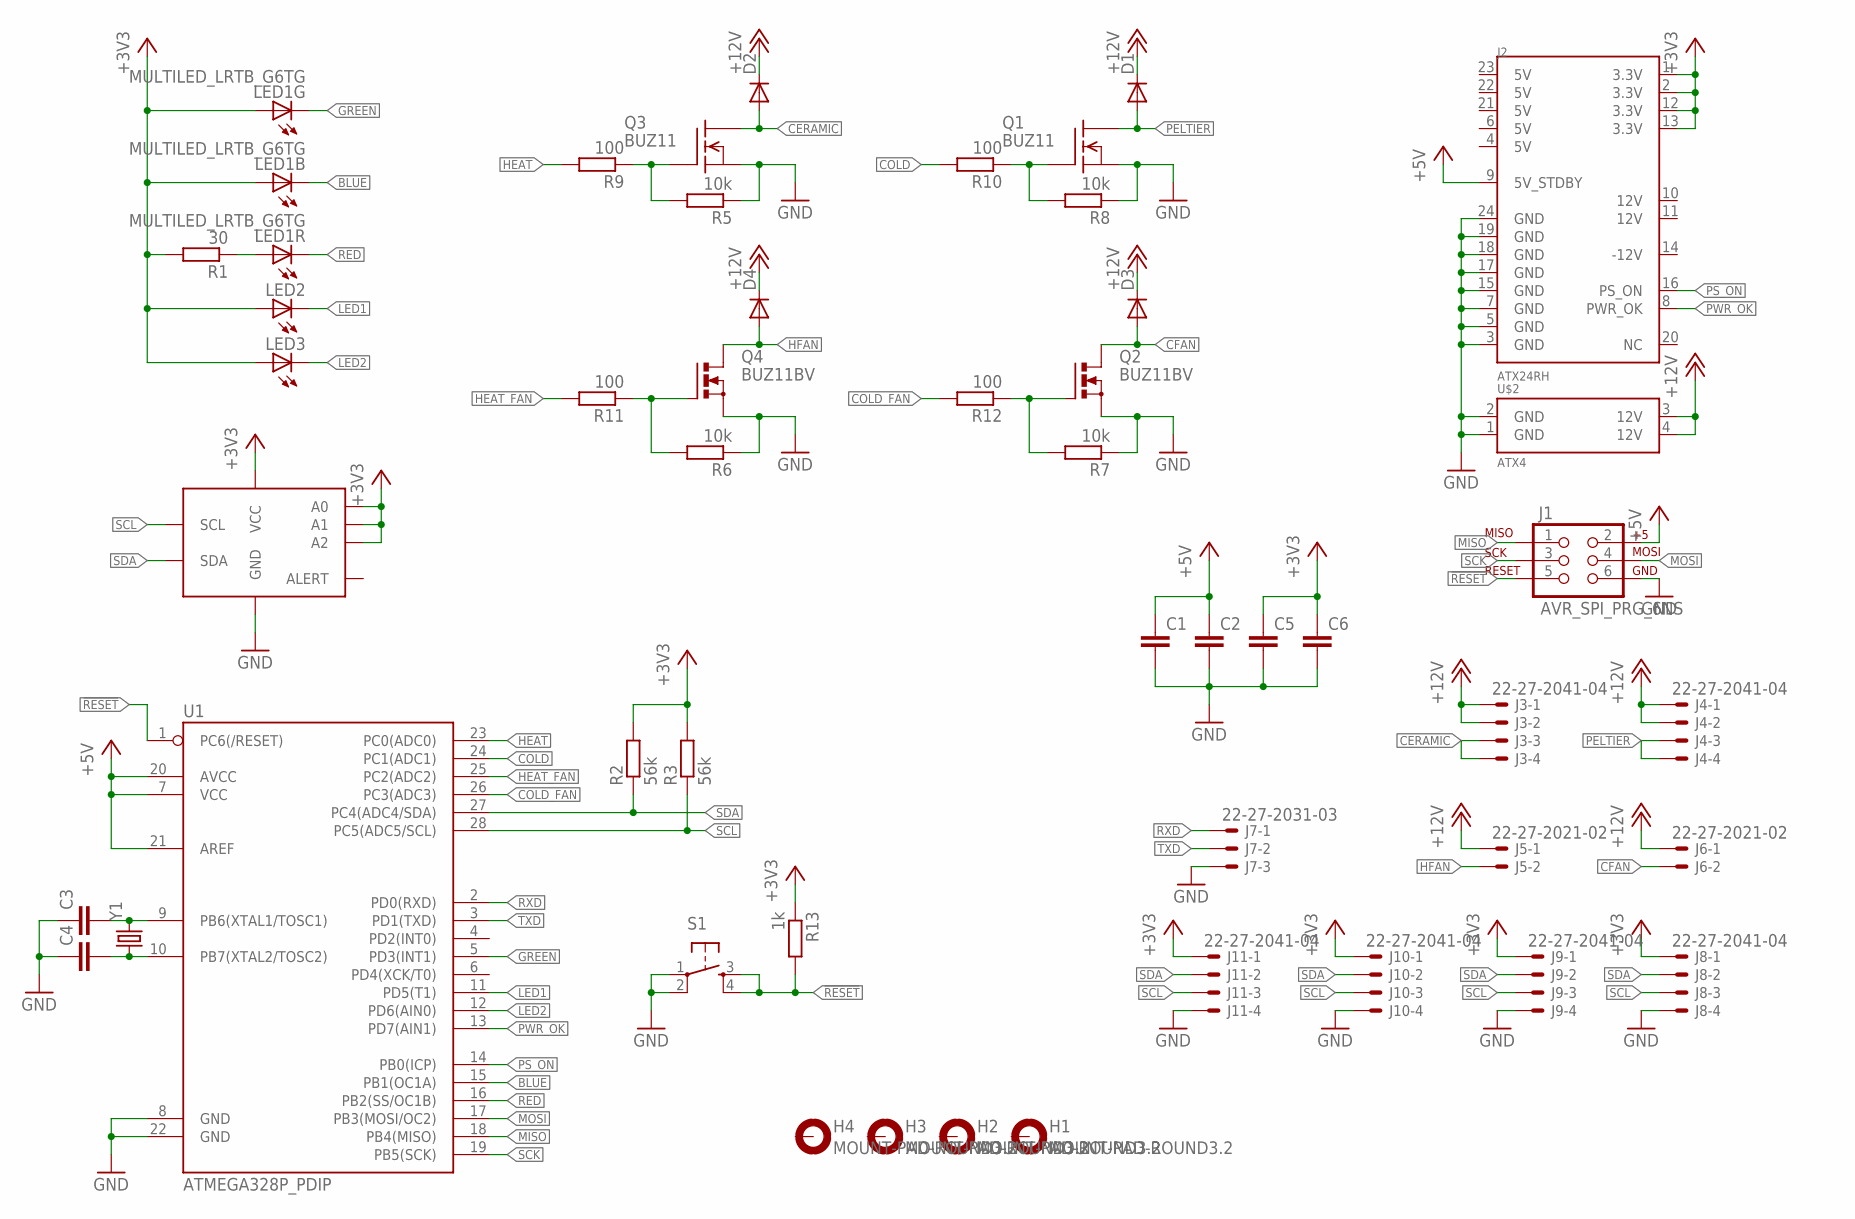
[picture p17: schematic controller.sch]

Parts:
C1, C2, C5, C6: C-EUC0603; C0603
C3, C4: C-EUC0603K; C0603K
D1, D2, D3, D4: DIODE-DO201-15; DO201-15
H1, H2, H3, H4: MOUNT-PAD-ROUND3.2; 3,2-PAD
J1: AVR_SPI_PRG_6NS; 2X3-NS
J2: ATX24RH; ATX24_RIGHT_ANGLE
J3, J4, J8, J9, J10, J11: 22-27-2041-04; 6410-04
J5, J6: 22-27-2021-02; 6410-02
J7: 22-27-2031-03; 6410-03
LED1: MULTILED_LRTB_G6TG; P-LCC-6_TOPLED
LED2, LED3: LEDSML1206; SML1206
Q1, Q3: BUZ11; TO220
Q2, Q4: BUZ11BV; TO220BV
R1: 30; R0603
R2, R3: 56k; R0603
R5, R6, R7, R8: 10k; R0603
R9, R10, R11, R12: 100; R0603
R13: 1k; R0603
S1: TAC_SWITCHPTH; TACTILE-PTH
U1: ATMEGA328P_PDIP; DIL28-3
U$1: TMP175; MSOP8
U$2: ATX4
Y1: CRYSTALHC49UV; HC49U-V

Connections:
!RESET: J1.5, R13.2, S1.3, S1.4, U1.1 (PC6(/RESET))
+3V3: C5.1, C6.1, J2.1 (3.3V), J2.2 (3.3V), J2.12 (3.3V), J2.13 (3.3V), J8.1, J9.1, J10.1, J11.1, LED1.A2 (A), LED1.A3 (A), LED2.A, LED3.A, R1.2, R2.2, R3.2, R13.1, U$1.5 (A2), U$1.6 (A1), U$1.7 (A0), U$1.8 (VCC)
+5V: C1.1, C2.1, J1.2, J2.9 (5V_STDBY), U1.7 (VCC), U1.20 (AVCC), U1.21 (AREF)
+12V: D1.C, D2.C, D3.C, D4.C, J3.1, J3.2, J4.1, J4.2, J5.1, J6.1, U$2.3 (12V), U$2.4 (12V)
BLUE: LED1.C3 (C), U1.15 (PB1(OC1A))
CERAMIC: D2.A, J3.3, J3.4, Q3.2 (D)
CFAN: D3.A, J6.2, Q2.D
COLD: R10.2, U1.24 (PC1(ADC1))
COLD_FAN: R12.2, U1.26 (PC3(ADC3))
GND: C1.2, C2.2, C3.1, C4.1, C5.2, C6.2, J1.6, J2.3 (GND), J2.5 (GND), J2.7 (GND), J2.15 (GND), J2.17 (GND), J2.18 (GND), J2.19 (GND), J2.24 (GND), J7.3, J8.4, J9.4, J10.4, J11.4, Q1.3 (S), Q2.S, Q3.3 (S), Q4.S, R5.1, R6.1, R7.1, R8.1, S1.1, S1.2, U1.8 (GND), U1.22 (GND), U$1.4 (GND), U$2.1 (GND), U$2.2 (GND)
GREEN: LED1.C2 (C), U1.5 (PD3(INT1))
HEAT: R9.2, U1.23 (PC0(ADC0))
HEAT_FAN: R11.2, U1.25 (PC2(ADC2))
HFAN: D4.A, J5.2, Q4.D
LED1: LED2.C, U1.11 (PD5(T1))
LED2: LED3.C, U1.12 (PD6(AIN0))
MISO: J1.1, U1.18 (PB4(MISO))
MOSI: J1.4, U1.17 (PB3(MOSI/OC2))
unnamed: C3.2, U1.9 (PB6(XTAL1/TOSC1)), Y1.2
unnamed: C4.2, U1.10 (PB7(XTAL2/TOSC2)), Y1.1
unnamed: LED1.A1 (A), R1.1
unnamed: Q2.G, R7.2, R12.1
unnamed: Q4.G, R6.2, R11.1
unnamed: Q1.1 (G), R8.2, R10.1
unnamed: Q3.1 (G), R5.2, R9.1
PELTIER: D1.A, J4.3, J4.4, Q1.2 (D)
PS_ON: J2.16 (PS_ON), U1.14 (PB0(ICP))
PWR_OK: J2.8 (PWR_OK), U1.13 (PD7(AIN1))
RED: LED1.C1 (C), U1.16 (PB2(SS/OC1B))
RXD: J7.1, U1.2 (PD0(RXD))
SCK: J1.3, U1.19 (PB5(SCK))
SCL: J8.3, J9.3, J10.3, J11.3, R3.1, U1.28 (PC5(ADC5/SCL)), U$1.2 (SCL)
SDA: J8.2, J9.2, J10.2, J11.2, R2.1, U1.27 (PC4(ADC4/SDA)), U$1.1 (SDA)
TXD: J7.2, U1.3 (PD1(TXD))

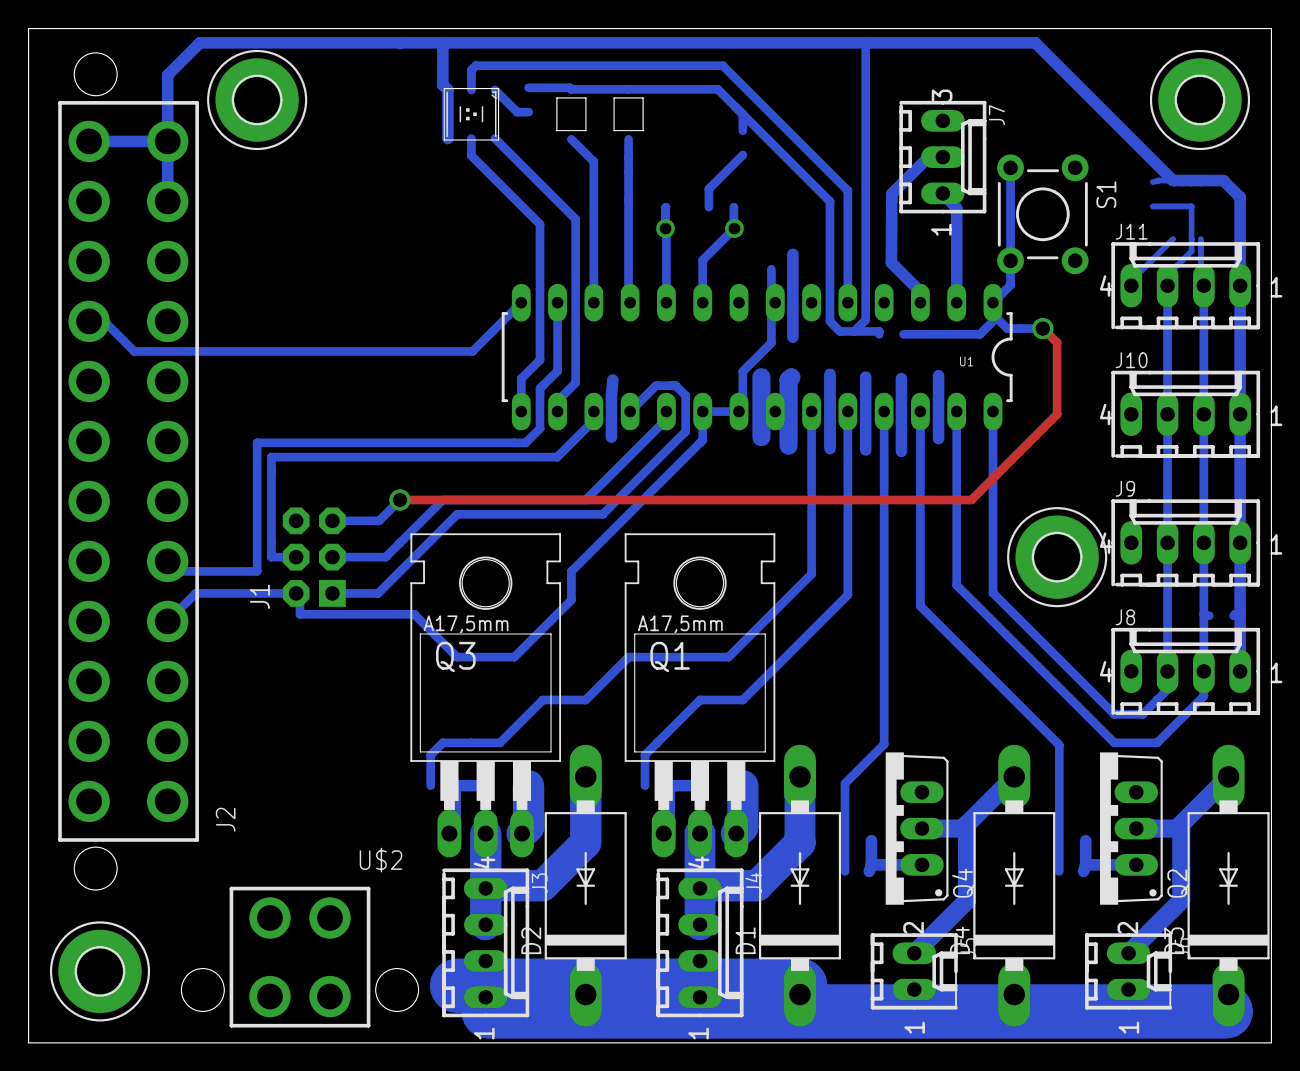
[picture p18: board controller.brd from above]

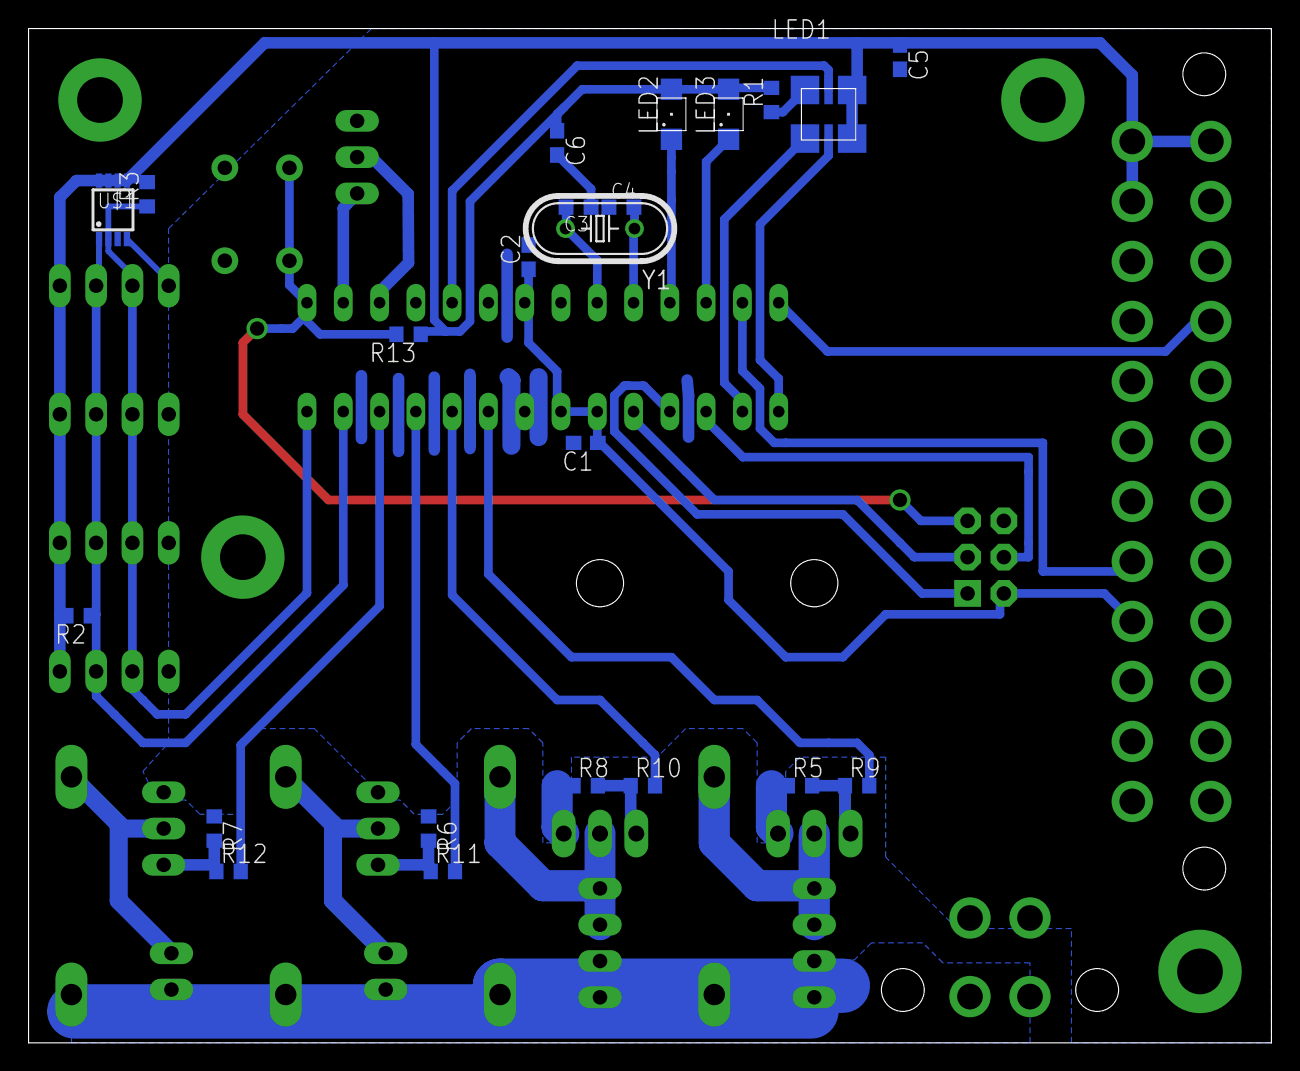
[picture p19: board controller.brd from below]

Board: 2 copper layers, 87.0 x 71.0 mm, 49 parts (23 on the bottom side), 34 nets.

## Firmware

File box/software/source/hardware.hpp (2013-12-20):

// coding: utf-8
/* Copyright (c) 2013, Niklas Hauser
* All Rights Reserved.
*
* The file is part of the my thesis and is released under the 3-clause BSD
* license. See the file `LICENSE` for the full license governing this code.
*/
// ----------------------------------------------------------------------------

#ifndef THESIS_HARDWARE
#define THESIS_HARDWARE

#include <xpcc/architecture/platform.hpp>

using namespace xpcc::atmega;

// IO #########################################################################
// ATMEL ATMEGA328P
//                    +-v-+
//     (!RESET) PC6  1|   |28  PC5 (SCL)
//        (RXD) PD0  2|   |27  PC4 (SDA)
//        (TXD) PD1  3|   |26  PC3 (HEAT_FAN)
//              PD2  4|   |25  PC2 (COLD_FAN)
// (GREEN,OC2B) PD3  5|   |24  PC1 (HEAT)
//              PD4  6|   |23  PC0 (COLD)
//              VCC  7|   |22  GND
//              GND  8|   |21  AREF
//      (XTAL1) PB6  9|   |20  AVCC
//      (XTAL2) PB7 10|   |19  PB5 (SCK)
//  (LED2,OC0B) PD5 11|   |18  PB4 (MISO)
//  (LED1,OC0A) PD6 12|   |17  PB3 (MOSI)
//     (PWR_OK) PD7 13|   |16  PB2 (RED,OC1B)
//      (PS_ON) PB0 14|   |15  PB1 (BLUE,OC1A)
//                    +---+

// Color
typedef GpioOutputB2 RedLedPin;
typedef GpioOutputD3 GreenLedPin;
typedef GpioOutputB1 BlueLedPin;

// Signal
typedef GpioOutputD6 WhiteLeftLedPin;
typedef GpioOutputD5 WhiteRightLedPin;

// Power
//typedef GpioOpenDrain<GpioB0> PsOn;
typedef GpioOutputB0 PsOn;
typedef GpioInputD7 PwrOk;

// Control
typedef GpioOutputC1 HeaterPin;
typedef GpioOutputC3 HeaterFanPin;
typedef GpioOutputC0 CoolerPin;
typedef GpioOutputC2 CoolerFanPin;

// Leds
#include "leds.hpp"
WhiteLedLeft whiteLedLeft;
WhiteLedRight whiteLedRight;
RedLed redLed;
GreenLed greenLed;
BlueLed blueLed;

xpcc::ui::RgbLed rgbLed(redLed, greenLed, blueLed);

// COMMUNICATION ##############################################################
// Message
struct
{
	uint8_t temperature0[2];
	uint8_t temperature1[2];
	uint8_t temperature2[2];
    uint8_t temperature3[2];
    uint8_t temperature4[2];
} rawSensorData;

// TMP102 and TMP175 drivers
#include <xpcc/driver/temperature/tmp102.hpp>
#include <xpcc/driver/temperature/tmp175.hpp>
/*
typedef GpioC4 Sda;
typedef GpioC5 Scl;
typedef I2cMaster Twi;
/*/
typedef GpioOpenDrain<GpioC4> Sda;
typedef GpioOpenDrain<GpioC5> Scl;
typedef xpcc::SoftwareI2cMaster<Scl, Sda> Twi;
//*/

// This sensor is always present
xpcc::Tmp175<Twi> sensor0(rawSensorData.temperature0, 0b1001111);

// these sensors are purely optional
xpcc::Tmp102<Twi> sensor1(rawSensorData.temperature1, 0b1001000);
xpcc::Tmp102<Twi> sensor2(rawSensorData.temperature2, 0b1001001);
xpcc::Tmp102<Twi> sensor3(rawSensorData.temperature3, 0b1001010);
xpcc::Tmp102<Twi> sensor4(rawSensorData.temperature4, 0b1001011);

// Serial debug
#include <xpcc/io/iodevice_wrapper.hpp>
typedef Uart0 Uart;
xpcc::IODeviceWrapper<Uart> outputDevice;

#include <xpcc/debug/logger/style_wrapper.hpp>
#include <xpcc/debug/logger/style/prefix.hpp>
#include <xpcc/debug/logger.hpp>
xpcc::log::StyleWrapper< xpcc::log::Prefix< char[10] > > loggerDeviceDebug (
		xpcc::log::Prefix< char[10] > ("Debug:   ", outputDevice ) );
xpcc::log::Logger xpcc::log::debug( loggerDeviceDebug );

xpcc::log::StyleWrapper< xpcc::log::Prefix< char[10] > > loggerDeviceInfo (
		xpcc::log::Prefix< char[10] > ("Info:    ", outputDevice ) );
xpcc::log::Logger xpcc::log::info( loggerDeviceInfo );

xpcc::log::StyleWrapper< xpcc::log::Prefix< char[10] > > loggerDeviceWarning (
		xpcc::log::Prefix< char[10] > ("Warning: ", outputDevice ) );
xpcc::log::Logger xpcc::log::warning( loggerDeviceWarning );

xpcc::log::StyleWrapper< xpcc::log::Prefix< char[10] > > loggerDeviceError (
		xpcc::log::Prefix< char[10] > ("Error    ", outputDevice ) );
xpcc::log::Logger xpcc::log::error( loggerDeviceError );

#undef	XPCC_LOG_LEVEL
#define	XPCC_LOG_LEVEL xpcc::log::DEBUG


// TASKS ######################################################################
#include "tasks/task_software_pwm.hpp"
task::SoftwarePwm<HeaterPin, 333> heater(whiteLedLeft);
task::SoftwarePwm<HeaterFanPin, 33> heaterFan(whiteLedRight);

#include "tasks/task_temperature.hpp"
task::Temperature temperature;

#include "tasks/task_temperature_control.hpp"
task::TemperatureControl temperatureControl;

#include "tasks/task_io.hpp"
task::IO inputOutput(temperature, temperatureControl);

#endif // THESIS_HARDWARE

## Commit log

2013-09-16 Add simple laser cur heater holder.
    [Heater_holder.dwg, Heater_holder.dxf]
2013-09-18 Add Controller Schematic and Board.
    [controller.brd, controller.sch]
2013-09-18 Hardware: Add fourth hole and different crystal footprint.
    [controller.brd, controller.sch]
2013-09-18 Software: Move hardware instantiation to own file. Add preliminary test Led classes.
2013-09-19 Add vector files for lasercut hardware platform.
    [Baseboard.dwg, Baseboard.dxf, Distance_rings.dwg, Distance_rings.dxf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]
2013-09-19 Update controller PCB.
    [controller.brd, controller.sch]
2013-09-19 Software: Add all Leds and heartbeat.
2013-09-19 Software: Fix Fast PWM Timer setup for Leds.
2013-09-20 Hardware: Add improved heater holder.
    [Heater_holder.dwg, Heater_holder.dxf]
2013-09-23 Software: Add SoftwarePwm Task for controlling Heater and Fan. Update xpcc.io.
2013-09-26 Software: Switch LEDs together with Mosfet.
2013-09-26 Software: Update Led inheritance. Remove heartbeat, as it was annoying.
2013-09-26 Software: Add temperature sensor and evaluation code.
2013-09-27 Software: Add temperature task to wrap all sensor code.
2013-09-27 Software: Add TemperatureControl task. Increase Temperature sampling to 250ms. Adapt HSV mapping to 20C (blue) -> 90C (red).
2013-09-27 Software: Update xpcc.io for Led fading time correction.
2013-09-29 Hardware: Redesign layout of controller PCB.
    [controller.brd, controller.sch]
2013-10-01 Hardware: Add reset push button to PCB.
    [controller.brd, controller.sch]
2013-10-01 Software: Move RGB Led driver to temperature task. Update xpcc.io.
2013-10-01 Hardware: Add Sensor Node holder. Add wind director. Update Baseboard, Fan and heater holder.
    [Baseboard.dwg, Baseboard.dxf, Fan_holder.dwg, Fan_holder.dxf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]
2013-12-17 Add code to dynamically add temperature sensors. Update xpcc.io.
2013-12-17 Add better way to parse desired temperature input.
2013-12-20 Exchange sensorList for a more efficient one. Nicer sensor outputs. Switch to SoftwareI2c as it is more robust to errors (by just ignoring them).
    Sensor addressing does not work reliably, only one additional sensor is attached.
    This might have something to do with pullups on SCL and SDA, since the cables
    are so long.
    Both Boxes have been tested and both the control loop and communication work.
2014-01-13 Move hardware/ folder into box/ folder.
    [Baseboard.dwg, Baseboard.dxf, Distance_rings.dwg, Distance_rings.dxf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]
2014-01-15 Add tested python temperature controller.
2014-01-17 Rename TemperatureController -> TemperatureControl.
2014-01-19 Fix box firmware. Output of temperature was missing a leading 0 sometimes.
2014-02-10 Add temperature input correction interpolation table.
2014-02-20 Add power output of heating element.
2014-02-22 Wait until mote also reached target temperature. Add mote temperature correction.
2014-03-30 Update Link Analysis: - Only one input type supported (StringMessage) - Link class filters rx messages - Fix multiple logger handlers in LinkAnalyzer class. - Add two more experiment parsers.
2014-03-30 Boxes without temperature controller can now be added. Make "wait temperature:" a separate command. Fix message length field in logging. Add experiment harness for 8 nodes.
2014-03-30 Add mote position hardware files.
    The mote positioner allows to accurately rotate and distance motes
    against each other. This should allow for better reproducible link
    properties.
    [length_bearing_6mm.dwg, length_bearing_bottom_3mm.dwg, length_connector_5mm.dwg, length_measure_5mm.dwg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]
2014-04-24 Add temperature test harness and scripts.
2014-04-29 Only heat boxes to 80C.
2014-05-01 Add thesis latex document.
    Add preliminary temperature box section with figures.
2014-05-07 String message can print itself now.
2014-07-16 Correct off-by-one error in temperature controller fractional clock generation.

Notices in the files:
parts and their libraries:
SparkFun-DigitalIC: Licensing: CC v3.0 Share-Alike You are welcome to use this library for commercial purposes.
